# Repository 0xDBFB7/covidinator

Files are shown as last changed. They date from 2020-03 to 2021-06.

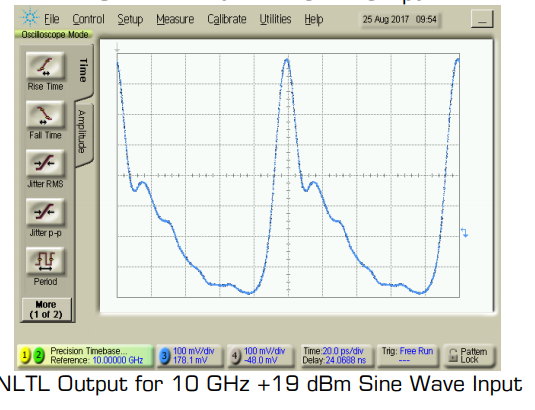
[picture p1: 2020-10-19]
electronics/propagation/NLTL_input_tone/Screenshot from 2020-10-18 20-32-23.png

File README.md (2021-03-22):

# Update March 2021

Now shifted focus to purely electroporative effects. Please see

# [Pure electroporation](https://github.com/0xDBFB7/covidinator/releases/download/vx.x/pure_electroporation.pdf) 

Thanks!

---

Hi! Welcome! There's not a whole lot of real substance here, but maybe you'll find something useful. I hope you like it! 

This was a (in retrospect, misguided) project to determine if extremely high electric fields can produce mechanical stresses sufficient to break the viral membrane (so-called electroporation). This doesn't seem to be necessarily *completely* implausible, but it's sufficiently remote (and TRL 0) that I'm not super interested in continuing work on it given circumstances.

```
<3   <3   <3   <3   <3   <3   <3   <3   <3   <3   <3   <3   <3   <3 
```

# [Terse summary](https://github.com/0xDBFB7/covidinator/releases/download/vx.x/summary.pdf) 
# [Full paper with supplemental, unfinished](https://github.com/0xDBFB7/covidinator/releases/download/vx.x/paper.pdf)

## References & Resources [HTML](https://raw.githubusercontent.com/0xDBFB7/covidinator/master/documents/references.html) | [Zotero (categories!)](https://raw.githubusercontent.com/0xDBFB7/covidinator/master/documents/references.rdf) | [BiBTeX](https://raw.githubusercontent.com/0xDBFB7/covidinator/master/documents/references.bib) 

```
<:  ^_^  :>  ^_^  :>  ^_^  :>  ^_^  :>  ^_^  :>  ^_^  :>  ^_^  <:
```

Things that are here:

 * A cheap (~$300) synchronous photon counting fluorescence reader - just a crappy plate reader/Gel-Doc/spectroflurometer without the spectro- part. 
    - Can instantly quantify sub-nanogram quantities of dsDNA using Biotium GelGreen (Xu et al's fast phage titer sampling, score!).
 * Li et al's 600-picosecond avalanche transistor Marx pulser
 * A few microbiology protocols - E. coli and T4 bacteriophage.
 * A cheap (~$300) 6-12 GHz microwave absorption spectrometer / scalar network analyzer. Almost useless for small signals, does not provide the SNR required for biological purposes, don't build one.
    - firmware/eppenwolf/runs: Data from a number of data-taking runs of the Eppenwolf.
 * A wrapper around flaport/fdtd's awesome electromagnetics library:
    - tissue.py: supports import of IT.IS Foundation computational phantom voxel files, with their supplied Cole-Cole dielectric model, for tissue simulations. Pretty rough, not formally validated.
    - PCB.py: A test of coupled NGSPICE - adaptive timestep and direct KiCAD netlist import and probe/source creation. Currently totally broken.
 * biology/JAMES/ A bespoke MD program thanks to the not-invented-here syndrome. Not enough time was spent exploring GROMACS and LAMMPS features for bead-spring elastic models. A complete waste of time. There is zero reason for this to exist.
 * Reasonably bad note-taking. When all this is over I wanna make a real sweet lab notebook, the current offerings aren't, in my opinion, super great - suggestions for features and workflows are welcome!

```
<3   <3   <3   <3   <3   <3   <3   <3   <3   <3   <3   <3   <3   <3 
```

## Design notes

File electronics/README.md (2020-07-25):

Milling settings:

30 degree carbide V-bit, 24 Krpm, 300 mm/min, 0.1 mm step-over, -0.1 mm step-down.

Check "Use aux. axis" in KiCAD gerber export, 

Todo: make a flatcam shell-file http://flatcam.org/manual/flatcamshell.html

G-code generated with FlatCAM, probed with Autoleveller 0.8.7 (bug in later versions),

then postprocessed with invert_probing.sh.

Board clamped to skim-cut MDF sheet and cut with regular scissors.

Paste stencils were laser cut from 80-weight black cardstock at 450 mm/min, 100%.

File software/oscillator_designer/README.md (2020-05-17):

To design an oscillator:

Install QUCS. QUCS 0.0.20 built from source was used.

```
git clone https://github.com/zonca/python-qucs
cd python-qucs
sudo pip3 setup.py install
```

Make a new ramdisk to avoid burning cycles on your SSD (or running into latency issues on HDD).

```
sudo mount -t tmpfs -o size=100m tmpfs /mnt/qucs-tmpfs/
```

and set net_file, net_file_modified, and data_file to that tmpfs. Also set QUCSDIR to your qucs installation path.

Design a circuit in qucs, and set schematic_file to the schematic.

This could be accomplished equally well with scikit-rf.

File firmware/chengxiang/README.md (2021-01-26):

Named Chengxiang after the team which characterized the Marx generator. (I know they weren't the first to use FMMTs as avalanche devices - I just happen to have lifted the design from them verbatim, so it seemed appropriate.)

sshfs deep:/home/arthurdent/covidinator/firmware/chengxiang/ mnt/

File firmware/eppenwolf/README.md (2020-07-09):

### The Eppendoofus

This is the firmware and host control software for the eppendoofus microwave-bio breadboard.

The d
s

the following types of messages are sent:

- Set VCO power
- ACK
-

a

Uses protobufs. Though I'm sure it exists, I couldn't find a simple
S.N.A.P protocol

Protobuf needs to be installed.
ARM_NONE_EABI doesn't like protobuf by default - no pthread! we therefore have to pass HAVE_PTHREAD=0

then we get an
google/protobuf/stubs/common.cc:50:2: error: #error "No suitable threading library available."
 #error "No suitable threading library available."
  ^~~~~
  https://groups.google.com/forum/#!topic/protobuf/WRA7uSZzC3c

Fortunately, pthread is only required in stubs/once.h; we just overwrite that, removing the relevant issues.

No go. needs lstdc++. Ultimately, just going to roll my own format.

We have to use Arduino's WString rather than std::string because of size limitations.

There has to be some packet-framing lib out there.
https://github.com/PowerBroker2/SerialTransfer - only 256 chars,

Have to remove #include "arduino.h" from SerialTransfer to mock

Now we have a real problem. We can't fit std::string on the teensy; but we can't include WString in the mocked build. So we'd either have to re-implement WString, or only use char*s, or give up on mocking.

I will do this last option.

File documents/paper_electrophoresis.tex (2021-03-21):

%!TeX root = paper_electrophoresis
\documentclass[paper.tex]{subfiles}
\begin{document}

\subsection{Paper electrophoresis}

There's a very interesting which has almost completely fallen into antiquity, and yet not obviously for any reason. Filter paper electrophoresis. It requires less work to set up than gel electrophoresis. because I believe it partially relies on a different mechanism. When power is applied to the filter paper baths, the buffer visibly pumps through. \cite{ELECTROPHORESIS1951} Electroosmotic flow 40 to 100 volts works fine, no gel needs to be poured beforehand.

I've heard that this is not effective for DNA et al, only for proteins or amino acids.

\cite{gelelectrophoresis}
\begin{fquote}
	While paper and other solid support materials proved to be an advantage over free solutions for the electrophoretic analysis of biomolecules, gels were adopted later because gels not only minimized diffusion better than paper supports they actually participated in the separation process by interacting with the migrating particles. Gels can be thought of as semi-solid matrices whose pore sizes aid in separation. The semisolid nature of the gel participates through a process known as molecular sieving. The three common media for gel electrophoresis are starch, polyacrylamide, and agarose. Of these, the starch gel medium is the least versatile whereas a wide range of separation effects can be achieved using the other two media. There are limitations to the use of both polyacrylamide and agarose but these are effectively minimized when the material to be analyzed is a nucleic acid. Even very small nucleic acids (i.e., oligonucleotides) are easily separated in an electrical field by one or the other medium. The primary criteria for choosing polyacrylamide or agarose gel electrophoresis are length and whether or not the nucleic acid is single stranded or double stranded. Short, single-stranded DNAs like oligonucleotides require polyacrylamide whereas long (>100bp), double stranded DNAs are best resolved on agarose.
\end{fquote}

The macgyver running buffer\cite{MACGYVER2005}.

\cite{Inexpensive1955}

\end{document}

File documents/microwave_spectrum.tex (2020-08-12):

\documentclass[paper.tex]{subfiles}% ===> this file was generated automatically by noweave --- better not edit it
\begin{document}

\clearpage
{\Large Experiment 1:}\\

\nwfilename{microwave_spectrum.pnw}\nwbegincode{1}\moddef{microwave_spectrum.py}\endmoddef\nwstartdeflinemarkup\nwenddeflinemarkup
import sys
sys.path.append('/home/arthurdent/covidinator/firmware/eppendoofus/host/')

import device_comms
import sweep

\nwendcode{}\nwbegindocs{2}\nwdocspar

It cannot be overstated how sensitive this measurement is. At 12 GHz, merely bringing one's hand near the coaxial line almost doubled
the power sensor reading.

\nwenddocs{}\nwbegincode{3}\moddef{microwave_spectrum.py}\plusendmoddef\nwstartdeflinemarkup\nwenddeflinemarkup
import random

\nwendcode{}\nwbegindocs{4}\nwdocspar

Positions of the three quantities on the slide are randomized\cite{first2000}.

\section{Preparation}

Autoclave

\nwenddocs{}\nwbegincode{5}\moddef{microwave_spectrum.py}\plusendmoddef\nwstartdeflinemarkup\nwenddeflinemarkup

\nwendcode{}\nwbegindocs{6}\nwdocspar

\end{document}
\nwenddocs{}

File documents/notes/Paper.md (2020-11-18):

## Field Limits

Exemption limits increase from 70 mW at 35 mm from the body to:

- at or above 6 GHz and the source-based, time-averaged maximum e.i.r.p. of the device is equal to or less than 5 W (adjusted for tune-up tolerance).

In these cases, the information contained in the RF exposure technical brief may be limited to information that demonstrates how the e.i.r.p. was derived.

At between 6 to 15 GHz, in an uncontrolled (public) environment, the Canadian government sets field thresholds at 61.4 V/m RMS. They also specifiy a limit adopted by most countries; 1 milliwatt / cm^2 (10 W/m^2) over a 6 minute averaging time, along with the following constraint:

> The total incident energy density during any one-tenth second period within the averaging time shall not exceed one-fifth of the total energy density permitted during the entire averaging time for a continuous field.

Controlled (occupational) limits are 50 W/m^2.

Uncontrolled electric field limits in Canada are 61.4 V/m and controlled is 137 V/m RMS. Yang et al's models for H3N2 specify a threshold at 86.9 V/m, but observe 40% inactivation at 87 V/m, and only 70% at 171 V/m (320 W/m^2) . All of those power densities are above even the controlled-environment power-density guidelines, at 20 W/m^2.

[https://www.icnirp.org/cms/upload/publications/ICNIRPrfgdl2020.pdf](https://www.icnirp.org/cms/upload/publications/ICNIRPrfgdl2020.pdf)

#### Exposure time

Both Yang and [] (apparently arbitrarily) chose a 15-minute exposure in their tests. To determine the effectiveness against airborne particles, and to minimize the power required in a dwelling phased-array beam, we must first establish the required duration of exposure.

As opposed to chemical inactivation, where the time dependence is dominated by viscous fluid dynamic effects [Hirose 2017], or ionizing radiation, where a certain dose of photons must be absorbed, 

As a damped, driven oscillator, the ring-up time of the virus depends on the Q factor. Yang et al. state the Q of H3N2 to between 2 and 10, so at 8 GHz the steady-state amplitude should be reached in well under 1 us.

Reality is rarely so tidy. [] have found a significant mechanical fatigue effect in phage capsids, where a small strain applied repetitively eventually causes a fracture. At low field strengths, this mechanism could extend the exposure required to break the capsid or membrane.

Variance in the sizes and stiffness of viruses (due to mutations) could shift the resonance off-peak, requiring a longer duration exposure or a frequency chirp to accommodate.

Other research[] has found T4 approximately a thousand times "easier" to inactivate chemically; however, its capsid is mechanically approx. 2x stronger than H3N2's envelope.

> [] obtain an excellent prediction using an elastic continuum method with a spherical virus, with opposite charges in core and shell.

We wished to gain more insight into the processes which cause the fracture, in an attempt to reduce the field requirements further.

Both coarse-grained bead-spring molecular dynamics (via integration of particle motion) and finite-element methods (via solution of governing elastic PDEs) have been used to great effect for simulation of mechanical properties of viruses. More recently, all-atom methods have also become computationally viable. An MD scheme was chosen for no particularly good reason.

The algebraic normal-mode methods included in many software packages [charmm] are not generally sufficient for this task, as they often assume the limit of low-amplitudes.

LAMMPS, GROMACS, OpenMM and HOOMD-blue were evaluated, and all could been made to work with some modification. However, because of difficulties in defining new force-fields for coarse-grained bead-spring modelling, because of the specific time-domain electric field impulses desired, and because of the multiple-run frequency sweep required to optimize the impulse, a custom simplistic MD code was written.

Unfortunately, electric polarization effects, (the redistribution of electrons)

The phage model was produced from raw CryoEM data using ProDy. ~~The coronavirid model was produced with LipidWrapper.~~

[] Each field seems to invent its own terminology for multiscale modelling. "coarse-graining" is referred to as DSMC.

[]: the use of special symbols in names seems to be problematic for searches. Hereafter we will refer to \phi 6 as Phi6.

----

It remains to be seen how much not-invented-here fallacy was baked into this project.

### [How long do T4 phages in the provided packaging last when refrigerated? Thanks!](https://www.carolina.com/viruses/coliphage-t4-t4r-living-5-ml/124330.pr#)

1answer

1. CBS Ben

   · 11 months ago  

   They can be refrigerated up to a year without any change in labeled titer.

double-wide, with 'resources' and 'figures' on the right pane? Emphasizes other documents
and figures more

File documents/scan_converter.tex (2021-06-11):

%!TeX root = scan_converter
\documentclass[paper.tex]{subfiles}
\begin{document}

\section{Scan converter}

\begin{autem}
This is an example of how the course of action can be distorted by engineering. In a non-pandemic scenario such a diversion might have been a reasonable. Indefensible. I am consoled that it did not account for more than 2 to 3 weeks of work.
\end{autem}

\begin{autem}
	This section is deliberately kept vague and without reference to construction details to avoid export restrictions. In any case, it is hard to imagine a technique fully developed and published in the 1940s would be of great secrecy now. 
\end{autem}

Because of the small sizes of viruses, all interesting time-domain spectroscopy results require resolving signals with greater than 10 GHz bandwidth.

So called "equivalent-time" or "sampling" oscilloscopes are less expensive; but it was hoped that it would be possible to resolve the breaking of the capsid - a transient, single-shot phenomenon -   A digital oscilloscope capable of real-time sampling such a transient is a tall order, and it did not appear that an undergraduate would be allowed access.

Gating time. Photoconductive gating is a particularly interesting technique for this.

There is also the concern that, when measuring a system producing kilovolt pulses using an instrument with an extremely electrically delicate 1V maximum input, some harm might come to a machine worth more than the experimenter. 

This turned out to be not unfounded - the kilovolt pulser used was observed to cause the RPi controlling the experiment to 

However, transient recordings of sub-nanosecond phenomena were made as early as 1938 by Manfred Von Ardenne using a "micro-oscillograph". By 1946, such oscillographs - now with bandwidths in excess of 10 GHz - were readily available commercially\cite{3beam1946}, and by 1949 found extensive use for quantitative measurements of ultrafast phenomena by Fletcher\cite{Production1949} and others. 

"Direct access" tubes to the logical conclusion. The design of Fletcher puts the cathode ray deflection plates essentially inside the.

The main practical limitations on oscilloscope sweep speed are discussed by Mackay\cite{New1948}, and are imposed by the Y axis deflection plate electron transit time and bandwidth (the X-axis speed is of less importance), and the beam current and sensitivity of the phosphor (faster sweeps reduce the electron flux and brightness of the dot).

\begin{figure}[H]
	%	\makebox[\textwidth][c]{
	\centering
	\subfloat[Damage to the sensor, believed to be due to. ]{
	
	
}
	\hfill
	\subfloat[]{
		
		
	}
		\hfill

	\subfloat[Direct electron beam detection]{
	
}
	\caption{Second.}
		\hfill

\end{figure}

\begin{figure}[H]
	\captionsetup{singlelinecheck = false, justification=justified}
	\centering
	
	\caption{}
\end{figure}

\begin{figure}[H]
	\captionsetup{singlelinecheck = false, justification=justified}
	\centering
	
	\caption{}
\end{figure}

The very high voltage actually makes this much easier

means that low-sensitivity diagnostics, like lithium niobate optical probes. Not having a suitable optical bench, an electron-beam probe, similar to a streak camera, itself similar in principle to scan-conversion digitizer tubes in Tek SCD and 7912 series transient digitizers.

If a low voltage sensitivity is required, and because modern high-pixel-density CMOS sensors allow the required deflection (and therefore the entire structure) to be minimized, these are simple to design and inexpensive (much of the complexity is in the slow-wave or travelling-wave structure which is usually required to match the signal velocity to the - slowing down light without affecting its properties or drawing power is an extremely difficult problem) and can offer sample rates in the terasamples/s and analog bandwidths of many dozens of GHz, albeit with very low vertical resolution. 

original von Ardenne 

\begin{fquote}[Livermore Operations][\cite{Scan2008}]
An internal CCD recorder would provide high sensitivity to the swept electron beam, but a CCD in a sealed vacuum tube has never been attempted or demonstrated in the phototube facility at Livermore Operations (LO). A prototype tube would most likely be built with a phosphor screen.
\end{fquote}

Possible routes:

make the plates super small like Von Ardenne (thin wires). see the papers on thin wires.

make the plates slow-wave structures matched to the speed of the electron; travelling-wave deflection plates.
unfortunately, travelling wave structures necessarily absorb power and affect the impedance of the circuit in question

multiple beams with different path lengths to have different phases?

put the x-axis at a 45 degree angle?

radiation damage to sensor 

Possibly some optical method. 

however, recording such transients is quite a solved problem, having been accomplished to the required degree 

taking "direct access" tube to its logical conclusion.

since the sensor will inevitably outgas, a sealed tube is impractical.

Low vacuum, gas focused tubes are less predictable and more difficult to model. XOOPIC; the standard PIC code WARP has undocumented feature of collisional ionization but Tegerup has a guide to use. Simulation

PIC-LAS

The distortion due to transit-time phasing is

$$ \frac{\sin(\frac{2\pi F \tau}{2})}{(2\pi F \tau)/2} $$

where $\tau$ is the transit time of the electron through the deflection region 

Image intensifier microchannel plates where angled holes cause secondary electron 

stray light 

old canal ray paper

the old WARP has a module for collisional ionization, though it's got a bug \cite{Simulation}.

\end{document}

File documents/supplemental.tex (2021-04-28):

%!TeX root = supplemental
\documentclass[paper.tex]{subfiles}
\begin{document}

\clearpage
%%%%%%%%%%%%%%%%%%%%%%%%%%%%%%%%%%%%%%%%%%%%%%%%
%%%%%%%%%%%%%%%%%%%%%%%%%%%%%%%%%%%%%%%%%%%%%%%%
\section[Appendix]{\Huge Captain's Log, Supplemental}

%%%%%%%%%%%%%%%%%%%%%%%%%%%%%%%%%%%%%%%%%%%%%%%%
\begin{fquote}[Paraphrased from W. G. Cochran][\cite{Statistical1953}]
The accumulated insight of a worker frequently merits recording when no documentation can be given.
\end{fquote}

%tonsil

\section{Sensing}

There is little discussion on microwave virus detection, with the notable exception of [Mehrotra 2019]. 

However, \cite{Microwave2012} find that - in controlled conditions - they can detect a single E. Coli bacterium in 50 uL of broth via a microwave cavity. 

Havelka \cite{Highfrequency2011} discuss microtubules.

With an extremely high power excitation pulse, the problem may become somewhat easier; especially if the virus has a ring-down that can be subjected to autocorrelation.

However, the dipole radiation power expected in even the most implausibly optimistic case would be about as follows:

$$P={\frac {\mu _{0}(2 \pi \cdot 20 GHz) ^{4}(0.5 \text{nm} * 10^6 e^-)^{2}}{12\pi c}} = 7.1 \times10^{-16} \text{W} $$

which for most reasonable conditions would $\approx 0.5 Janskies$, meaning that the power radiated from the virus would be considerably overpowered by the milky way.

% (magneticConstant*(2 pi * 20 GHz)^4 * (0.1 nm * 1000 * electronCharge)^2)/(12*pi * c) -> W

Materials

polycarbonate

infinitely autoclaveable. However, clear has possible issues with flurosescence background. white 
is 
generally recommended for fluro. 

polypropylene
autoclaveable, although softening causes warping if not supported. Difficult form strong bonds to 
with adhesives. causes "hairs" when machining.

Rationale for doing this alone. Science is nothing without collaboration. However, it's also nothing without acknowledging the shortfalls of your research. There remains no physical reason to expect this to work - it is indistinguishable from crackpottery - and, in fact, the first route of investigation did not work. Therefore, seemed irresponsible to redirect resources or involve other people.

at least that's the story I tell myself.

There is some good advice in the Government Accountability one is especially sage:

"Be as quantitative as possible."

source of truth in the home lab. For instance, you can build an oscilloscope, or a pulse generator, 
but not both. 

\subsubsection{Old papers}

many of the base facts - and some of the most useful and simplest methods - are in the early 
papers, and later papers generally just refer to the previous ones. it can be of some use to try to 
find the earliest papers. 

For instance, when searching for methods for the bacteriophage, lots of modern detail-scarce papers 
appear, but none of the most important Delbruck papers. Books are one way to side-step this issues

When searching for old papers, use the terminology of the day. millimicrosecond, for instance, for 
nanosecond".

find government gray-literature publications on the topic. They are often 

find research groups with "lists of publications".

\subsubsection{Cargo-cult}

For in-vitro research, it seems to me that perhaps this field is running into the issues Feynman's rat-races \cite{Cargo}. There are a large number of very tricky variables. Requires analysis fo the very details of how the study was conducted, rather than simply its results. While the measurements 

Of course, we commit the very same mistakes and fall into the same traps, we are not immune from criticism.

In some cases, these are thoroughly characterized and described. UWB rat paper. 

But it seems to me that each worker (myself included!) is using their own test arrangement; and yet the studies are not so different as to require such customization.

It occurs to me that perhaps a set of exquisitely characterized standardized test cells and procedures would be helpful; and a requirement that any papers on the topic either use such a cell, or if their study requires some exceptional treatment, to follow an established procedure to add a new cell to the standard. 

Alternatively, methods such as the optical hetrodyne one,

If possible, very specific buffer compositions should be made universal.

What heating patterns can be expected from a certain microwave input? What modes can be introduced by deviations in machining tolerances?

Then, of course, are the questions of the excitation: what brand of attenuators are satisfactory?

Of course, one cell could not suffice for the whole range of microwave frequencies.

There is also the matter that the scientific publishing infrastructure could perhaps provide for a "scientific lineage". We often hear of a "scientific record": journals will retract a paper from "the record"; but where {\it is} this record? Where is the chain of trust upon which new results can be added? Each paper is forced to supply its own context; each worker is forced to re-dredge the entire chain of truth, to discover the controversy which clouds some papers; each offers its own interpretation of the literature. It is inevitable that some history will be lost; that the wrong starting point will be taken up; a veritable fork in the literature. Especially as the volume of scientific research increases as society proceeds. The only data is a few references per paper, and a date for each! Another such record exists in comprehensive books written by workers on the topic.

But is this not an artifact of the limitations of printed journals, whereby papers must necessarily be individual entities? Is there no way by which papers can be arranged so that they each supply a visible part of the jigsaw, where each paper brings with it the complete story of the field?

Scite.ai and similar services, but it feels like these are tacked-on workarounds to re-add metadata which should have existed in the first place.

Consider the non-thermal effects literature. It starts, perhaps, in the 1800s; 

\clearpage
%%%%%%%%%%%%%%%%%%%%%%%%%%%%%%%%%%%%%%%%%%%%%%%%
{\Large Optical centrifuge polarization chirp}\\
\begin{multicols}{1}
%%%%%%%%%%%%%%%%%%%%%%%%%%%%%%%%%%%%%%%%%%%%%%%%

\includepdf[
    %% Include all pages of the PDF
    pages=-,
    %% make this page have the usual page style
    %% (you can change it to plain etc). By default pdfpages
    %% sets the pagecommand to \pagestyle{empty}
    pagecommand={\thispagestyle{empty}},  
    %% Add a "section" entry to the ToC with the heading
    %% "Quilling Shapes" and the label "sec:shapes"
    addtotoc={1,section,1,Quilling Shapes,sec:shapes}]
%% The pdf file itself
{optical_centrifuge.pdf}

\includepdf[
%% Include all pages of the PDF
pages=-,
%% make this page have the usual page style
%% (you can change it to plain etc). By default pdfpages
%% sets the pagecommand to \pagestyle{empty}
pagecommand={\thispagestyle{empty}},  
%% Add a "section" entry to the ToC with the heading
%% "Quilling Shapes" and the label "sec:shapes"
addtotoc={1,section,1,Quilling Shapes,sec:shapes}]
%% The pdf file itself
{biology.pdf}

\end{multicols}

Contrary to some [Hardell 2017] reports, we do not find the FCC and ICNIRP to be significantly affected by special interest groups; their rationales appear to be transparent.  [FCC-19-126A1], for instance, is a particularly entertaining memorandum:

\begin{quote} 
	
Similarly, IEEE-ICES urges the Commission to adopt a higher SAR exposure limit of 2 W/kg averaged over 10 g. [snip] We are not persuaded that the IEC standard should be adopted at this time.", "Medtronic and the AAMI-CRMD recommend a more relaxed threshold of 20 mW. We decline to increase the 1-mW threshold.". 

\end{quote}

Things heating up at the Microwave Safety fandom.

\clearpage
%\rule{\linewidth}{0.2pt}
%
%
%There seems to be a discrepancy between \cite{Efficient2015} and our reading of [C95.1-2005].
%
%They use a threshold in open public space of $100(f/3)^{1/5} \text{ W/m}^2$. The 115 W @ 6 GHz figure they provide corresponds to this equation with a coefficient of 100.
%
%For Table 9, general public, the equation is $18.56 (f)^{0.699} \text{ W/m}^2$, or $64.93 \text{ W}/\text{m}^2$ @ 6 GHz. 
%
%Different versions of the IEEE standard have used equations of equivalent form but with different coefficients [Wu 2015]; it is entirely possible that we have retrieved the wrong standard.
%
%\rule{\linewidth}{0.2pt}

\section{Wherein a wideband oscillator is designed}

Several incorrect pieces of information conspired to lead us to try to develop an inexpensive ultrawideband oscillator.

\begin{itemize}
	\item The
	\item The assumption that a broadband frequency sweep would drastically improve the inactivation threshold, and moreover that 
	\item The ideal 
	\item The assumption that the only commercially available oscillators in this frequency range were expensive YIG-tuned devices.
\end{itemize}

Besides the AD (formerly Hittite) HMC732 device, ADF5355 and lmx2615

There are really two different conflicting criteria: 

A low-cost, wide-band

Unfortunately, designing wideband microwave circuits is significantly more difficult than for a particular frequency. Quarter-wavelength 

Varactor diodes are a GaAs hyper-abrupt junction diode.

We were warned that this would be difficult: 

CEL did not supply a SPICE model for the GaAs FET device used in early prototypes. A FET was originally because a gate is ostensibly easier to bias than a base; but this turned out to be unfounded.

[Steenput 1999] has an interesting analytic method to synthesize a SPICE model suitable for a transient simulations from S-parameter measurements using negative resistances. However, this neglects the I/V characteristic. 

[Polyfet 1998] describes a simple optimization method to synthesize a SPICE model for an active device, and CEL appnote provides some details for GaAs devices.

\rule{\linewidth}{0.2pt}

OpenEMS is excellent, with Python bindings, some lumped components, and mesh refinement. However, embarrassingly, we were not able to resolve all the dependency issues in order to install it.

\paragraph{Biasing}\

In our simulations, the varactor-tuned feedback circuit appeared to be particularly sensitive to the introduction of bias-tees. 

The gate must be weakly pulled to ground, otherwise stray charge destroys the oscillation.

\fancyhead[C]{style 1 with thin line}

With 0.79 mm FR4 substrate and 0.2 mm (8 mil) wide traces, the maximum impedance achievable was about 115 ohms, which did not appear to be sufficient as an RF choke. Use of defected grounds can increase inductance, but this was not evaluated.

If suitably high-impedance traces are not available, a common technique is to use a quarter-wavelength line (approximately 6 mm long with the above parameters at 8 GHz) terminated with a stub to produce a virtual short or open circuit [Seo 2007]. 

However, reflections from these structures still appeared to distort the frequency/phase response beyond repair, even with ostensibly wideband stubs [Syrett 1980].

\noindent\fbox{\parbox{\linewidth}{
	Rebuke: despite this blather, many other papers have had success with bias-tees at these frequencies.
}}

Alternate methods evaluated, failures: 

In production, these could be accomodated by graphite-polymer printed resistors. 

Odd-pole varactor-loaded combline filters appeared to have excellent phase and frequency response; however, the geometry necessitates low-inductance via stitching to the ground plane.

%\noindent\fbox{\parbox{\linewidth}{
\begin{autem}
	{\it autem} Others have had great success with varactor-tuned comblines, especially non-grounded lines.
\end{autem}

[Tsuru 2008 fig. 10] is an excellent review of various oscillator designs.

The parasitic inductance of common varactors appears to become problematic at these frequencies (but not for non-wideband use).

\paragraph{\textbf{Spacing}}\

FDTD results still yielded some coupling at 2 mm isolation.

\paragraph{\textbf{Via stitching}}\

Rather than the almost universal technique of via stitching components immediately to the ground plane (a tedious process with our prototyping setup), a large ground pour on the component layer was used wherever ground was needed, as mentioned in [Hunter? combline]. Since we use microstrip rather than coplanar waveguide, 

Since the ground plane does not participate in the DC bias at all, no vias are required in the final device. This means that the drilling, electroless strike and electroplating steps are unnecessary for production.

\PRLsep{{\itshape The wideband oscillator }}

Not having access to any RF equipment, we needed an oscillator tunable over the X-band.

There are many oscillators. The HB100 uses a dielectric resonator, for instance; cavity-based methods with mechanical tuning; active antennas using. 

The literature is quite mature, partly due to the FCC's recent ultrawideband communications guides.

As a result of our gross incompetence, the oscillator was designed via an inane, roundabout, and fiendishly tedious manner, and our description of this technique only contributes to the field by being suitable for a dartboard; our analysis can only hold water when combined with paper mache; and a lesser invertebrate in posession of a copy of Grebennikov's excellent Microwave Oscillator Design would have accomplished the task faster.

Designing an oscillator of this type in one step with a few kindergarten equations appears to be well within the reach of modern network analytical techniques. Genetic algorithms are quite well matched to this problem, and many commercial software packages are  [computer microwave design book]. 

We began experimentally by building a scaled version of [Mueller 2008]'s active antenna crudely with copper tape, using a CEL [] GaAs FET.

We then manually tried a number of filter designs, using the manufacturer's S-parameters and QUCS' microstrip approximations. This intially appeared to yield good agreement with experiment. Peaks in the feedback voltage simulation corresponded approximately with peaks in the observed spectrum. [figures from LO prototype N]. 

A crude, inane, and extremely disorganized trial-and-error procedure was performed for many weeks. A wide variety of analytical methods for filter design were attempted [documents/global.ipynb], but simultaneously obtaining the correct phase shift and frequency response was somewhat difficult. Adding the parasitic inductance of the varactors always seemed to destroy our most perfect creations.

Using an SIR filter has the added advantage of confusing epidemiologists.

Eventually, QUCS, zonca/python-qucs, and scipy's basinhopper were used with a cost function somewhat similar to that described in [Kaplevich]:

\begin{verbatim}
    freq_coeff = 1
    phase_coeff = 1.5
    ratio_coeff = 0.5
    insertion_loss_coeff = 0.2
 
    frequency_cost = freq_coeff * (abs(desired_center_frequency-fb_peak_frequencies[0])/1e9)
    phase_cost = phase_coeff * abs(1.0 - phase_at_peak)
    ratio_cost = ratio_coeff * fb_peak_ratio
    insertion_loss_cost = insertion_loss_coeff*(1.0 - fb_peak_values[0])
    cost = frequency_cost + phase_cost + fb_peak_ratio + insertion_loss_cost
\end{verbatim}

Optimizing first for the high frequency, fixing the inductor and microstrip values, and then optimizing for the varactor values at the low frequency.

This produced a seemingly acceptable feedback loop (note the group delay / phase progression):



However, when this was built, varactor tuning performance was abysmal, with hops and peaks; and the tuning range was far smaller than expected.

It was thought that a transient simulation - to determine how the spectrum actually evolved - would improve the situation. 

As of 0.0.20, QUCS' microstrip models are not yet compatible with transient simulations; and some improved filter designs required simulating coupling between more than two microstrips, which QUCS did not yet support natively.

\begin{figure}[H]

\end{figure}

The complete transient simulation matched reality very closely. 

\begin{figure}[H]
	\includesvg[width=\textwidth]{wideband_LO_2_simulated_tuning}
 	\caption{"Wideband VCO 2": BFP620  \\
 	 Oscillator tuning simulated with electronics/ngspice/oscillator\_designer\_2.py commit <>, eLabID 20200613-d28a8004c...}
\end{figure}

The oscillator design is a testament  This highlights that a computation is not a substitute for understanding.

The key sticking point seems to be that as frequency increases, using microstrip design techniques, the parasitics of any filter structure are so large that the small change in impedance that the varactors can provide does not tune the circuit by any meaningful amount.

The two varactors on each tuning circuit each contribute 0.7 nH and between 0.35 to 2.4 pF; each blocking capacitor contributes about 0.2 nH. The frequency range of the oscillator can be selected by adding between 0.5 nH to 1.5 nH symmetrically to both tuning circuits. 

"Using the lead inductances of the bipolar transistor and varactors provides the required value of the base inductance".

Indeed, [Tsuru 2008]'s "tuned circuit" in Fig 8 is, in fact, just the varactors, plus an almost invisible high-impedance line.

The final oscillator is a 'wideband double-tuned varactor VCO', based almost verbatim on [Tsuru 2008] and the reference design in Figure 8.36, p378 of [Grebennikov 2007]. 

The rest of the papers in the bibliography were highly enlightening regarding the principles of microwave oscillator design.

For ease of design and simulation, selecting a device with both Touchstone S-parameters and SPICE models is greatly preferable.

It is commonly claimed that FR4 is a 'slow' substrate, and that the high loss tangent of ~0.02 makes it unsuitable for microwave systems.

However, with this PCB substrate, the expected loss of only 0.026 dB/mm on signals of minimum 0 dBm is patently acceptable. As viruses do not have a discriminating palate, we are also only minimally concerned with $S_{11}$ reflections, noise, or spurs, so precise impedance control is not required; the wideband VCO sweep accomodates for any variations in resonant frequency due to wide manufacturing tolerances.

This topology of oscillator worked marvellously on essentially the first try.

Not having a good analytical understanding, we resorted to using a purely computational method.

In addition, the design of wideband feedback-loop VCOs is a relatively well-explored field, and many reference designs exist. 

Merely scaling designs like [] was not effective.

Several analytical filter design methods were 

This is apparently known as a "double-tuned" wideband.

Oscillators must meet the Barkhausen criterion:

\begin{itemize}

\item A 360 degree phase shift around the feedback loop (including the phase shift contribution from the amplifier, which itself varies greatly with frequency)
\item A loop gain $>1.$ 

\end{itemize}\
%
However, in practice a third element is also required:
%
\begin{itemize}
\item A frequency-selective element that restricts oscillation modes and decreases phase noise.
\end{itemize}
%

With large feedback-loop structures, such as long PiN-switched phasing lines, proximity effects from nearby flesh were found to detune the oscillator significantly.

 design of a triple-tuned oscillator.

\paragraph{}
The buffer amplifiers 

\rule{\linewidth}{0.2pt}

In case you're wondering, like I was, why the voltage coefficient of capacitors 

\rule{\linewidth}{0.2pt}

Much of this project was done in 1.5 mm microstrip with a 2.5 to 3 mm routed isolation. However, it became apparent that the inductance of vias with the ground plane was too great. It has been suggested that low-inductance vias in prototypes \cite{Microwavee}

Grounded coplanar waveguide, where the primary ground plane is on the top side of the board, presents many advantages, and in later testing appeared to provide much better performance and easier design. connectors can interface with the top side; trace sizes are much more compatible with small SMD devices.

\rule{\linewidth}{0.2pt}

Again, inductive choke biasing in the feedback loop was practically impossible. Biasing PiN diodes with a 10kohm resistor, (with 330 ohm safety resistor) one to 48V bias and another through an 2N7002P N-channel mosfet worked fine. 

The oscillator ran fine with a PiN bias of 2.34 mA. [LO prototype N]. A high bias voltage of 48V was required to get sufficient current through the two 10K resistors and the PiN diode to obtain a low impedance while remaining delicate with the vfb.

The PiN diode used has a resting resistance of 500 ohms, 5 ohms at 2 mA and 2 ohms at ??. 

48V is a little tight on the 50V rated voltage of our DC blocking capacitors.

Each activated PiN diode should be biased separately, since putting 2x 2 mA through 20K would take an impractical 80V.

\rule{\linewidth}{0.2pt}
%
%Conductors are represented by zeroing all components of the electric field in those regions. 
%
%There are many different possible source geometries, each introducing their own distortions.
%
%There are many ways of linking SPICE and FDTD. 

\rule{\linewidth}{0.2pt}

Bandpass filters can be designed by first designing a low-pass filter prototype (usually Chebychev) (or, in our case, using reference filter component tables), and then transforming this low-pass into a band-pass. [Hunter 2001] is an excellent overview of this process, with many design examples for different filter topologies. 

The coupling coefficient between two low-pass filters determines the band-pass bandwidth.[Hui 2012]

[Hunter 2001] also describes an analytical method to create a filter with the precise group delay - phase shift versus frequency - required for stable oscillation. However, simultaneously compensating for the group delay introduced by the amplifier itself (nearly 180 degrees over the frequency range for the CEL part) seemed complex.

Phase shift can be introduced either via a length of microstrip, or a high-pass/low-pass filter [Microwave101]. Adding a fixed microstrip line restricts the tuning range, however, and the filter inevitably affects the frequency response.  

%\rule{\linewidth}{0.2pt}
%
%NGSPICE's KSPICE coupled transmission lines require the capacitance and inductance per unit length in Maxwell matrix form, rather than the physical $C_{even}$/$L_{even}$ (each line's capacitance and inductance to ground) and $_{odd}$ (between elements) form provided by tools like wcalc. "matrix not positive definite". [Schutt-Aine] discusses this; we reproduce here for convienience.
%
%\[ L_{11} = L_{22} = L_{even}  \]
%\[ L_{12} = L_{21} = L_{odd}  \]
%\[ C_{11} = C_{22} = C_{even}+C_{odd}  \]
%\[ C_{12} = C_{21} {\it{(unused)}} = -C_{odd}  \]
%
%\rule{\linewidth}{0.2pt}
%
%In practice, the timestep required to obtain convergence in particularly tight corners of the SPICE simulation can drop to 1e-20, which is far below the Courant limit of the FDTD simulation. To eek out a bit more performance, a simple adaptive-timestep technique from [ a ] is used; we simply set the timestep so that the maximum change in voltage per timestep from the SPICE portion is less than 
%some threshold.

\PRLsep{{\itshape Sampling time-domain spectrometry}}

\begin{quote}
A rapidly increasing voltage step V tŽ . is applied to the 0
line and recorded, along with the reflected voltage R tŽ .
returned from the sample and delayed by the cable propagation time Figure 2 . Any cable or instrument artifacts Ž .
are separated from the sample response due to the propagation delay, thus making them easy to identify and control. The entire frequency spectrum is captured at once,
thus eliminating drift and distortion between frequencies.
\end{quote}

The pulse is usually recorded in real-time with a many-GHz oscilloscope. However, by using a sampling oscilloscope, massively undersampling the signal,

Another advantage of this technique is that no high-Q filters are required to select the frequency;
discrimination is in the time-domain, and is spread out over many seconds. It is also much easier to generate a 10+ GHz fast edge than it is to generate a CW signal.

\PRLsep{{\itshape Power amplifier }}

The amplifier and oscillator are separate for ease of design; this way the phase response of the amplifier is of no consequence. 

Our target power for the test is about 0.01 W, mandating a $2 \sqrt(2)$ V peak to peak RF swing on the Z=50 output.

The $V_{CEO}$ breakdown of the bipolar transistor in question is only 2.3V. Above this value, current begins to flow from the emitter to the base, turning on the transistor and causing thermal runaway. If the base bias has a low enough impedance and can source current, this $V_{CEO}$ can be violated safely. [Toshiba, Bipolar Transistors, some other paper on the strong base bias]

One solution would be to match the output to a lower impedance [Leuschner 2010]:

\begin{quote}
Generating high RF power from low supply voltages poses also another problem: the optimum load impedance of the PA output stage transistors becomes very small. A matching network with a high transformation ratio is needed to transform the antenna impedance of 50 to the optimum load impedance. High transformation ratios usually result in small bandwidth and higher losses. Possible solutions are the use of either non-standard high power RF devices or special circuit topologies using only the available standard devices.
\end{quote}

Use of so-called stacked, HiVP, or collector-feedback cascode designs can also allow the RF voltage to be distributed over many devices.

It should also be noted that when stressed, these devices can fail with a slow power-output degradation over weeks, an effect not usually found in lower-frequency designs. 

%\printbibliography[heading=none, title={}, keyword={amplifier}]

%
%\clearpage
%\PRLsep{ Wherein antennas are characterized}
%
%Method-of-moments solvers like NEC-2 are the standard for simulating these sorts of antennas. However, most commonly-available packages don't seem to handle multiple dielectric constants, such as the air and substrate of a patch antenna.
%
%The impedance of a structure over frequency can be determined in FDTD by:
%
%\begin{itemize}
%  \item Applying a gaussian pulse to a voltage source - in our case, applied to a via connecting the path (or probe)
%  \item Running the simulation until the transients have all died out below some threshold, while logging the source voltage and current at each timestep
%  \item Taking the fourier transform of the (real) excitation voltage and current (producing a complex result, mind you)
%  \item Taking the magnitude of the ratio of the two complex spectra.
%\end{itemize}
%
%This is the computational equivalent of dropping a piano off a balcony to see which key is stuck.
%
%See [Penney 1994], [Luebbers 1992], [Luebbers 1991], [Luk 1997]. 
%
%Our implementation is in \ghfile{electronics/simple_fdtd/runs/U.py}.
%
%A similar mismatch to the SPICE exists for fourier methods - but in the other direction.  The courant limit often demands fine timesteps, but since each FFT bin is $ f_{bin} = n_{bin} / (N_{simulation} \ dt) $ , the majority of the FFT bins exist into the hundreds or thousands of GHz, leaving no resolution in the low-frequency domain of interest unless $N_{simulation}$ is extremely large - even if all the transients in the simulation have died down, you still have to keep the sim running to make the FFT happy! 
%
%There's more than enough 'information entropy' in 4000 FDTD points for most antennas. But you need some 30,000 points to get 10 bins below 20 GHz!
%
%There are a few methods of changing the FFT bin size artificially, which [Bi 1992] reviews. You can "use a manual fourier integration over the frequency region of interest".
%
%But, in a staggering turn of events which will presumably be familiar to statisticans and preposterous to everyone else, a far simpler method is to {\it discard} 95\% of the data, by down-sampling to 1/10th or so.
%
%An equally simple method that seemed to produce better results in our case is to pad the voltage and current samples to the correct length. The jump discontinuity introduced by padding with zeros has a negligible effect.
%
%It's so thumpingly unintuitive to me that adding 50,000 zeros to a 5000 value dataset can improve the resolution of a measurement by 300-fold.
%
%It is important to remember to normalize the gaussian pulse, or else numerical noise will be introduced. The magnitude is not important - [Luebbers 1992] use 100v, others use 1v, etc.
%
%Though uneven dt FFTs exist, the time step can be constant at the courant limit for this simulation.
%
%A step impulse (1 first timestep, 0 otherwise) has been used in some works, though in our case performance was quite horrid.
%
%A correction factor due to the staggered magnetic field of the Yee lattice must be introduced; [Fang 1994]. Their $Z_2$ equation (correcting for spatial inaccuracies, but not temporal) was sufficient.
%
%
%This technique is equivalent to that used in electrochemistry, known as fourier impedance spectroscopy - except they seem to usually use a known impedance source rather than a hard source, presumably because ideal hard sources don't exist in reality.
%
%Allowing the simulation to run for long enough that all transients dissipate is important for accuracy - deceptive dips in the current can cause early termination. A surprising amount of detail is contributed by even the smallest current levels. Our threshold is 1e-7 amps for 700 iterations.
%
%[Samaras 2004] has a very useful set of experimental and FDTD data for calibration and comparison. Comparing a probe via source in the different positions, we obtained agreement of $\sim 7\%$ in impedance and $\sim 5\%$ in frequency.
%
%The use of a hard source feed-port affects the number of timesteps required by introducing unphysical transients. Using a port with a virtual 50-ohm resistance reduces the computational requirements by a large factor; see [Luebbers 1996].
%
%Simply monitoring the source current during the simulation is somewhat deceptive. Periodically monitoring the change in the fourier transform seems to be a better convergence metric.
%
%The units of the FFT (unlike those of the continuous FT) remain in volts.
%
%\rule{\linewidth}{0.2pt}
%
%Most equations in papers on the FDTD method are supplied without making the scaling factors explicit; some need multiplying by the Courant number, For use with flaport/fdtd the H-field to current line integral in [] requires scaling by $\mu_0 * (dx/dt)$, where $\mu_0$ is the vacuum magnetic permittivity, dx the cell size, and dt the timestep - despite the equation already possessing a deceptive set of $dx$-es.
%
%FIX THIS IT'S WRONG
%
%Naturally, if one is competent, this discrepancy will be immediately obvious. Those not dimensionally-intuitive, such as myself, find it useful to run dimensional analysis using a unit-aware calculator such as {\it sharkdp/insect}.
%
%\rule{\linewidth}{0.2pt}

\begin{quote}
With four parameters I can fit an elephant, and with five I can make him wiggle his trunk.
\end{quote}
- von Neumann  

with six parameters, you can do it with only physical constants. Beware numerology.

\rule{\linewidth}{0.2pt}

Most passives (inductors, capacitors) companies supply S-parameters for their parts. Use them.

\rule{\linewidth}{0.2pt}

This has nothing to do with , but it's an amusing parlor trick that I accidentally ran into while trying to carbothermally reduce copper oxide powder. It led me to the SiC susceptor resonator, so it wasn't a total waste.

Add a thimblefull of fine copper powder to the bottom of a mason jar. Cover the mouth with a layer of Kapton tape. Next, inject pure argon gas for a few minutes, then seal the tape fully.

Put the whole shebang in a friend's microwave oven. 

Wait patiently. There will be a sizable bang and a terrific plasma.

My hypothesis is that this is due to the higher ionization energy of Ar. Air seems to slowly leak in, decreasing the 

\PRLsep{{\itshape The antenna itself }}

The impedance of a patch antenna varies with position on its surface. Probe feeds to a specific point on the patch

Unfortunately, patch antennas have a relatively narrow bandwidth.

\rule{\linewidth}{0.2pt}

\PRLsep{{\itshape Power sensing }}

The diode detector power sensor is based on the Infineon appnote [] and [], itself based on a circuit from The Art Of Electronics. 

A detailed description of various diode detectors are found in []. Because the steady-state current through the detector is very small, the microstrip can simply be terminated in the standard manner.

The Mini-Circuits ZX47-40-S+ would be an excellent low-cost COTS alternative.

%\printbibliography[heading=none, title={}, keyword={rectifier}]

\PRLsep{{\itshape Microfluidics: small channels, big headaches }}

We had anticipated having to perform a large number of tests for optimization of the impulse. Automating tests also has the advantage of removing operator bias, and (in our case) minimizing artifacts from the sample holder. Since all the components were already computer-controlled, it seemed little extra effort.

We originally planned on using techniques from the rapidly accelerating field of centrifugal microfluidics, using a broadband patch antenna smaller than the cuvette, and measuring transmission through the cuvette.

Centrifugal microfluidics has the advantage of getting a pump for free; mixing can be effected by generating vortexes by accelerating and decelerating quickly; and because everything is circular, it is easier to design equidistant.

The most important feature is the consistent "down" vector; because capillary forces 

However, aligning seemed liable to produce artifacts; runout in the spindle;

Sterilization is often effected by cytotoxic gas []. UV we resorted to autoclaving, warping.

Th edges are charred; however, we have not found any discussion of toxicity of the laser cut edges, so we assume they're fine.

In a crude version of transmission welding. Tx welding usually relies on one material being transparent, and the other opaque - clear and black plastics, for instance. We obtained nearly useable results by scuffing one surface and rubbing in fine graphite powder.

Both the hydrophobicity / wetting angle of the substrate (useful for valves with a certain threshold pressure, among other things), the adhesive surface energy, and sterilization can all be effected by UVC exposure. Unfortunately, we were not confident in the homogeneity of the 

Not all plastics can be laser welded.

3DuF; this is an excellent program 

The final process was as follows:

Just using a single-sided tape over micromachined channels didn't work for us; the tape remains sticky and stuck to the bottom of the channel, blocking it.

\begin{itemize}
	\item 1/16" 003 size Viton O-rings McMaster-Carr \#9464K103, 
	\item 3M 467MP 0.051 mm double-sided adhesive transfer tape with 200MP acrylic adhesive, DigiKey 3M9726-ND.
	Various other tapes were tried, such as 9495MP; the laser was not powerful enough to cut these.
	While the intermittent temperature rating is over 121 C, the high-pressure steam environment does seem to degrade any exposed regions of tape.
	
	A CO2 laser is usually used to cut these otherwise transparent materials. We only had a diode laser. However, the front and back paper liners absorb sufficient laser power to melt the tape between. This produces horrible results, but was sufficient for this purpose. With our 2.5 W, ~0.15 mm spot size, 450 mm/min for the tape.
	
	\item MG Chemicals 416-T Laser Printer Transparency Film, 0.1 mm thick. Presumably a PET/Mylar material.
	
	\item A vinyl cutter was used to cut the openings in the top mylar cover slip.
	\item Frame machined from polycarbonate with a 1/16" two-flute carbide endmill, 24000 RPM, between 500 and 1000 mm/min, up to 1.5 mm step-down. G-code generated with MeshCAM. This seems to withstand the autoclave without any damage.
	\item Note: the tape preferentially sticks to the back liner, rather than the front.
	With both adhesive liners on, rub the thing hard with a rounded edge and rolling pin.
	Aluminum foil tape backing on the adhesive layer.
	Don't de-weed yet. 

\end{itemize}

Note that cutting many of these materials with a laser is a bad idea. The residue will 

\begin{itemize}
	\item Tape mylar to a cardstock backing with masking tape on the sides. Cut mylar on plotter with InkCut. 175 g force. 
	\item Apply aluminum foil tape to the rear backing (with "3M" text) of the adhesive transfer tape. This supports the cut structures, without being cut itself.
	\item Stick the adhesive to the laser bed with Kapton, foil-side down. It's not a good idea to use masking tape; it'll catch fire.
	\item 
\end{itemize}

Making this device ourselves was a grave mistake that potentially cost many lives. We should have used \cite{Straight}, a COTS version which we discovered halfway through. 

I'm sorry.

\paragraph{Lessons learned:}

When trying to characterize the response to some process parameters (say, laser power), iteratively trying different parameters in series can be somewhat useful, as each trial informs the next. In this instance, we would try a speed and power, unstick the material from the bed, observe the result, decide on the course of action, and repeat. However, if it is possible to try many parameters in parallel just as fast as in series, (that is, in our case, make a coupon using [] that tries all reasonable values simultaneously), it would be very dumb not to do this.

We are very dumb.

\printbibliography[title={General fluidics resources}, keyword={microfluidics}]

\printbibliography[title={Centrifugal}, keyword={centrifugal}]

\PRLsep{{\itshape aaaaa }}

One problem with the formal, academic paper format is that one starts to believe what is written, which is a death sentence for accurate reasoning. We try to avoid this by being unprofessional.

\label{para}
\ref{para}

\clearpage
%%%%%%%%%%%%%%%%%%%%%%%%%%%%%%%%%%%%%%%%%%%%%%%%%
%{\Large Microwave Musings}\\
%
%	%%%%%%%%%%%%%%%%%%%%%%%%%%%%%%%%%%%%%%%%%%%%%%%%
%	
%	\noindent\fbox{\parbox{\linewidth}{
%			Toolchain:
%			\begin{itemize}
%				\item Failed oscillator feedback-loop optimization toolchain: QUCS 0.0.20 + python-qucs + scipy's 'basinhopper'
%				\item Successful A slightly modified ngspice + ngspyce + pyEVTK
%				\item gprMax for FDTD EM simulation
%				\item KiCAD, wcalc, scikit-rf, ngspice
%			\end{itemize}
%	}}
%	%
%	
%	
%	Microwave design has a reputation for being the purview of wizards. Modern RF software packages like HFSS, Microwave Office, Agilent's ADS, and Mathworks' RF toolbox, for which; component models 
%	
%	Luckily, this project falls perfectly within the subset of microwave technologies that do not require a goatee. The vast majority of the behavior of most circuits can be accurately modelled with the very same SPICE tools as one would use at low frequencies. With judicious application of reference designs, it seems to be possible to design 
%	
%	Before about 2005, however, it seems to have been somewhat the norm to write a simple numerical code to solve the problem at hand based on underlying principles.
%	
%	We are also aided by the fact that what took a \$150,000 computing cluster a single decade ago can now be done in a few minutes by a single budget GPU.
%
%
%
many programs try to implement their own command scripting language
if the api doesn't expose fast access to the data on each timestep, then you're limited to the features that have already been implemented

\section{Timeline}

\paragraph{Comments by others}

\Acrobatmenu{GoBack}{Back}

\end{document}

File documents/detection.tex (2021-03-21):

%!TeX root = detection
\documentclass[paper.tex]{subfiles}
\begin{document}

\begin{autem}
	I hasten to note that culturing and quantifying viral titer is a completely solved problem, and is a procedure often done in kindergarten labs. The amount of time and effort we spent on this problem was completely unjustifiable. It was driven by an acute lack of competence, equipment, and the 0.8 uL volume constraints of our original poorly designed microwave setup.\\
	
	None of the techniques that we mention are even remotely novel, and we present only the barest of experiences with each.
	Indeed, the fluorescence technique that were eventually decided on is common practice for lysis detection; our use is not novel in the slightest.
\end{autem}

Most of our methodology results are tainted by two factors:

First, the fridge froze. A small "three-way" 

T4r+,

Lack of optical with

this means that small changes in volume, position, 

\section{E. coli host culturing}

\begin{figure}[H]
	\captionsetup{singlelinecheck = false, justification=justified}
	\centering
	
	\caption{
		\light{
			\\
			We've got a thing\\
			that's called\\
			{\it Radar Love}\\}
		We've got a wave\\
		in the air}
\end{figure}

Essentially the only method of determining the activity of phage is to have it infect a suitable host. Host range

Typically, this is done either in a large tube or a flat-sided optical cuvette.

Because the variation in the optical density is quite small, this poses some rather. 

A lot of the basic facts of phage, and most of the useful techniques were determined in the 1930s. 

A small vial of liquid has a much larger surface area relative to its thermal mass. sis removed, the temperature drops very rapidly; if the temperature drops outside the "physiological range" of around 33-40 C, growth is stunted \cite{effect2003}. \cite{growth1946}. I'm not sure if this was the problem I encountered, 

As a faculative aerobe, E.coli requires a concentration of oxygen to be present in the mixture for speedy replication \cite{Effect1965}; and this supply must also be kept sterile. One method to ensure this is by using a bubbler aerator; Carolina recommends an aquarium pump with cotton-ball filters. Probably Syringe filters are a good alternative.

Another method, often used in microfluidics\cite{Microfluidic}, is that of \cite{method1951}; the Manganese dioxide catalyzed decomposition of hydrogen peroxide. $MnO_2$ is readily obtained from alkaline batteries; and in this case no sterility issues are presented. However, it is not obvious how antimicrobial $H_2O_2$ vapor can be prevented from contacting the culture.

Bottles of zero air may be more effective.

In commercial fluid transfer machines, this is often resolved by HEPA filtering the input to an enclosing cabinet.

Shaking incubators, where the flasks are 

Ensuring that a great deal of headspace was present in a sealed tube (that is, culturing 2.5 mL in a 15 mL falcon tube) was sufficient for brief, low-density.

As the size of the well decreases, the Reynolds number also decreases \footnote{In fact, in the case of a circular well, it's not obvious that this is the case - the cross section decreases faster than the characteristic length}, and turbulent flow is greatly hampered.

Even slight rotation of the tube, such that the graduations 

"Chromogenic" substances \cite{Fluorogenic1991}, or the degradation of various dyes like Methylene Blue; tetrazolium dye methods;

Using 2.5 mm diameter x 3 mm high wells cut in polycarbonate and sealed with clear packing tape. However, the presence of small bubbles in the headspace of the wells prevented a consistent reading.

We tried simply adding 1 uL of culture to the microscope slide;

The 8-bit resolution and dynamic range of most cameras did not seem sufficient to discern the turbidity; and masking and correcting for 

\cite{Vision2016} use an ingenious technique. A background with sharp light-to-dark edges is used. Slicing the image into chunks only slightly larger than the object,

The 0.8 uL sample in each was not sufficient to produce a measurable change in turbidity in a 0.2 uL - or we were not experienced enough to perform the phage lysis protocol properly.

However, we were not able to make smaller volumes of culture enter the log phase.

Another very interesting technique is that of \cite{Study2003}, 

\subfile{paper_electrophoresis}

It should be noted that 

\subsection{Detect the growth of the host, and measure effects of the virus on that growth}

\subsubsection{Plaque assay}

The plaque assay for viruses has remained essentially unchanged since d'Herelle and Delbruck's era.

Advantages over broth methods are the apparently longer infective period without agitation or 

Contamination - in both directions: if you don’t wash your hands properly before working, you might end up with a thick soup of some truly horrific bacteria.

Despite poor aseptic technique, contamination was not a serious issue - perhaps 1 contaminant region per plate.

Incubating the bacterial lawn for sufficient contrast to read the plaques imposes a ~1 to 3 day delay between test and results. Each test requires several dilution tubes

\subsubsection{Protocol and observations}

\begin{toolchain}

To simplify and for higher throughput we use the drop-cast absorption protocol of \cite{Simple2018}, which uses only a single layer of 1\% agar.

150 mL water in a 250 mL beaker covered with alu foil, with stirring, and boiled in a pot of water. 1.5 grams of nutrient agar powder \footnote{Seaweed Inc, Amazon} was added to 150  until molten. A magnetic stir bar was used to ensure all was fully melted,
and then the beaker was autoclaved for 15 minutes. After cooling to 60 C for 25 minutes in a water bath on a hotplate, 20 mL of agar was poured onto [100 mm?] polystyrene plates. The plates were left to set, then dried inverted with a flamed bent copper wire spacer for air exchange at 70 C for [1 hours?].
The plates were then stored inverted in plastic bags at 4 C until use.
\footnote{How agar percentages are specified seems somewhat ambiguous to me - is the percent of the agar itself (a viscosity measure), or the nutrient-agar mix (a growth measure)?
	Weight/weight? It appears to be w/v of the whole dry powder in distilled water.}

After cooling, 1 mL of overnight culture was poured across the plate, excess drained onto the next plate, and allowed to dry for 35 minutes at room temperature.

A control plate was made with pure stock phage and autoclaved phage.

The sample was retrieved from the cuvette by carefully removing the tape backing and withdrawing 0.8 uL from the reverse side, to avoid a silicone oil bubble.

Unfortunately, this ended up being very inconsistent.

Not having a 10 uL pipette, the 0.8 uL sample of phage was diluted in 7.5 uL of sterile broth in a microplate, then all 7.5 uL was added in 2.5 uL steps to the agar.

\st{Each 0.8 uL sample was diluted in 0.2 mL of nutrient broth, a 250x dilution. If the $10^6$ pfu.}

60c to pour was I think too high - condensation was high, even after 1 hour at 37c no change.

". The dryness of the agar is very important; if too moist, the
drops will run and coalesce, if too dry, the bacteria will grow
poorly"

The plates were dried at ~70 C in an oven with the slightly open.

The plates were incubated overnight. The lawn was very nicely formed; the phage concentration was

It was difficult to tell where the drops were placed, and they ran together.

\begin{figure}[H]
	\captionsetup{singlelinecheck = false, justification=justified}
	\centering
	
\end{figure}

\end{toolchain}

\subsubsection{Broth assays}

This, however, requires a microplate reader which can simultaneously agitate for sufficient oxygen, incubate, and 

Tetrazolium dyes are metabolized 

GFP

\subsubsection{Impedance assay}

Because it would be difficult to maintain temperature on and multiplexing was difficult, low-frequency E. coli culture monitoring impedance spectra were performed separately.

An ultra-simple KHz impedance spectrometer was built, following \cite{unconventional2015}.

Purely contactless, capacitively coupled impedance measurement was found to have an unworkably small signal level;
however, a single conduction path and a single capacitive coupling through the Kapton film yielded a 10 mV signal level with 5V Vpp drive. A 110x amplifier was used to bring levels up.

0.7 mm gold-plated spring pins ('pogo' pins) pierced the silicone oil layer and pressed against the bottom tape; 1.4 mm pads were the second electrode.\footnote{Platinum, gold wire, anodized aluminum, or graphite would likely have worked equally well.} The pins were wiped with 99\% alcohol before each test.

2.5 uL stationary e. coli culture was added to 5 uL broth and 2.5 uL phage or autoclaved phage.

0 - 3 were phage; 4-7 were autoclaved phage.

Failure. decrease in signal rather than the expected increase, and no difference between autoclaved and phage.

Looking at this later - the fluid has leaked out of the wells after some time. That might be why this didn't work.

\section{E. coli flavin autofluorescence}

Added 2.5 uL to 5 uL broth. There does seem to be an fluorescence signal from; 100 uS long pulse, -70 mV is a good threshold.
Hz w/e.c, 2.9-5 Hz broth

Put the original eppendorf culture full of e. coli in. Jumped to 18 Hz @ -81 mV! Fantastic!

Thought I was all clever-like, using the oscope trigger out as the comparator and plugging that into a counter,
but above 20 Hz there's no thingy.

No. No go.

Weird background noise.

" By moving into this hydrophobic environment and away from the solvent, the ethidium cation is forced to shed any water molecules that were associated with it. As water is a highly efficient fluorescence quencher, the removal of these water molecules allows the ethidium to fluoresce.[citation needed]"

Otherwise, GFP-flouresecent strains of E. coli, or phage which has been labeled with a 

\subsection{Detect the release of intracellular material due to the lysis of the host}

One common target is the enzyme $\beta$-galactosidase. E. coli and other. Both  isopropyl $\beta$-D-thiogalactoside. Lactose itself is a reasonable substitute (Borralho \cite{Lactose2002}).

Ijzerman

X-gal \cite{Improved}

X-gal is only soluble in DMF and DMSO. We choose DMSO due to DMF's toxicity. DMSO is miscible with water, so that works out nicely. Solutions of < 0.75\% DMSO seem to not be cytotoxic.

I was introduced to this by Ijzerman \cite{liquid1993}, who recommend chlorophenol red $\beta$-D-galactopyranoside (CPRG) as the chromogen for a high sensitivity. CPRG is very hard to obtain except through Sigma.

beta-galactosidase

\begin{figure}[H]
	\captionsetup{singlelinecheck = false, justification=justified}
	\centering
	
	\caption{The very pretty opalescent blue culture caused by E. coli B trying to metabolize lactose in an X-gal $\beta$-galactosidase enzyme indicator.}
\end{figure}



 It’s probably in principle possible to synthesize them yourself, but it’s totally impractical. You will probably need a corporate address HS codes. 

T4 has a comparatively huge genome, which makes this easier.

\subsection{Detect the lysis of the virus, and the release of intra-viral material}

A fingerprint, for instance, has only about 0.2 ng of DNA (Subhani), so contamination is not a huge issue.

Phages release several small compounds like putrescine and spermadine when broken (Minagawa\cite{characteristics1961}). These can be indicated colorimetrically at ppm scales with ninhydrin, or at nanogram scales via fluorescamine. 

Biotium Gelgreen has a very specific advantage: to increase the safety of the dye, the flurophore is tied to some huge proprietary molecule, preventing it from diffusing through membranes or capsids. This has the side effect of making the fluorescence intensity strictly related to the quantity of genomic material dispersed in the solvent, rather than 

\subsubsection{Nucleic acid UV extinction }

The 260 nm extinction due to 60 MDa DNA at concentration $10^8 = 10e-9$. With a 1 mm path length is 0.002x. that's going to be swamped by everything else.

\subsection{Directly detect the virus itself}

PEG apparently concentrates to $10^{12}$ or 13 no matter what the starting concentration is (huh?), very convenient.

Early workers on phage mention\cite{ADSORPTION1940}  that cultures with a titer above about $10^10$ have an opalescent blue tint due to Tyndall scattering. Schlesinger in 1933 \cite{Beobachtung1933} (paper is in German). This technique appears to have been forgotten?

Concentrated can be put into the microgram range of high-sensitivity protein assays like BCA or Bradford, but that requires propagation and PEG precipitation, plus many such assays pose disposal hazards and stain labware. 

\end{document}

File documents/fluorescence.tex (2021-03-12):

%!TeX root = fluorescence
\documentclass[paper.tex]{subfiles}
\begin{document}

\begin{figure}[H]
	\captionsetup{singlelinecheck = false, justification=justified}
	\centering
	
	\caption{}
\end{figure}

\begin{figure}[H]
	\captionsetup{singlelinecheck = false, justification=justified}
	\centering
	
	\caption{}
\end{figure}

the base had integral overcurrent protection, which was triggered a few times during development - a very useful 

For one thing, GelGreen appears to be eminiently stable - samples can be stored for long periods of time; pre-mixed batches. 

Unlike luminescence techniques, 

%\subsubsection{Light source}

A modulation frequency of 

Lexan fluro was unex

Acridine orange (N-alkylacridinium)

Orange 16 

Fluoris
 
 LOL
 
(apologies to Floris Laporte)

sketches of light source in inkscape

from [], using ImageJ to stack. works great on cheap cmos cameras - interestingly doesn't work at all on more expensive cameras. - 
almost good enough - great for diagnostics

interestingly, the fact that the camera has color is quite valuable; filtering the green out can increase sensitivity a lot

a 30-s exposure on a cheap camera also almost got there.

Should make a discord as lab notebook

virus-specific

hemagglutinin test

the microscope is largely unnecessary. 

bleaching was not obviously an issue, nor was storage with the dye bound to DNA.

A white LED with a high color-rendering index (DK) seemed to have more power in the blue passband; however, green leakage around the filter was too strong. 

Unlike gels or plastic-glass sandwiches as used by Tiffen, thin-film filters have the disadvantage that the pass-band depends greatly on the angle of incidence.  

$$\lambda = \lambda \sqrt{1-sin(\theta)^2}$$

The wavelength shifts shorter (bluer) as $\theta$ increases.

This isn't an issue for the excitation filter, but is an issue for the.

Since the LEDs and flurophore emissions are not naturally collimated, this poses a little bit of an issue.
The microscope objective seems to provide sufficient collimation for the emission filter.

The Edmund filter was unmounted glass. Also, these thin-film filters do not extend to the edge of the glass. Edge-blankening ("inked") fil

The LED was about 3 cm away, and put through a ~3 mm aperture in a piece of PVC pipe. The output from the filter was directly into the 1 mm fiber, itself improving the bandpass.

The 10 nm FWHM emission filter is much narrower than professional GFP filters, especially the super-wide edge-pass ones; a lot of photons are lost that way. However, it's still more than sufficient. 

it has been noted that water is a good fluorescence quencher and that this might be how 

If time-domain filtering is sufficient, 

Low background is required.

Xu's method \cite{Quantification2020}

Performance of this arrangement was very satisfactory. A 10-second integration time, with, produced a background fluorescence signal of ~1500 counts, with per-sample stability of approximately $\pm 1500$ counts. The  

Contrary to standard microscopy, you want as little excitation light to enter the objective as possible. Using the existing 

autofluroescneces Lexan

Nanodrop, using 280 nm absorbance. They're also \$10,000.

the input edge is considered a clock; the minimum pulse width limits apply, but are not clearly specified in the datasheet. In this case (1/155 mhz) = 6 ns.

However, we had no luck with precipitation.

Luckily, a recent paper has the answer: direct fluorescent detection of DNA in solution, outside using dyes that bind to (intercalate into) DNA. GelGreen doesn’t penetrate.

As noted by [xi?], this is a saturating effect; if too many flurophores intercalate into the DNA the fluorescence is weaker. A “1/4000” solution of GG in distilled water mixed 50/50 with the sample (“1/8000”) worked great in our case.

(Phi6 uses an RNA - many dyes have different responses to single-stranded (ss)DNA, dsDNA, or 

autof

With the setup we’re using and the small quantities, the excitation light is somewhere around ~$10^5$ times as powerful as the emission. This doesn’t seem to be a big issue gel-docs, picking out bands on gels - they don’t usually seem to use excitation filters; however, to get the excitation bleed-through low enough to do this quantitative assay, the bleed-through must be really low, and in our testing proper dielectric filters are required on both the excitation and emission sides. 

There are a few sources of noise:

PMT dark counts
Some be filtered out by judicious use of comparator pulse height threshold, the lock-in takes care of it. A non-issue in our case.
Ambient light leakage
Using microscope optics and the lock-in, essentially a non-issue for use, surprisingly. Some fluorescence microscopes use micron-size apertures to limit the depth of field to avoid Putting 
Figure out the average current limit for your PMT, the expected voltage based on your load resistor value and watch that it never exceeds it. It’ll be fine. Even with the room lights

Note that PMTs are happy to endure very high pulse currents, like flashbulbs for exciting; no shutters or anything required. Gating the photomultiplier HV is another technique.

The PMT was at maximum sensitivity (in fact, slightly above max voltage)

Gel-docs , with spectra specified using the Wratten scale. These filters alone do not seem to have optical density (OD - logarithmic value of transmission in the blocking band) values sufficient for this qfluor. 

Most commercial microscopes use dichroic beamsplitters, allowing the excitation and emission beam to go through the same objective. The dichroic only removes the excitation to the 1\% level - you still need the dielectric filters, and they’re really expensive. With fiber optic excitation at right angles to the objective, excitation scattering was low enough that the dichroic was unnecessary. 

The fiber optic \cite{vurek1982nanoliter}

You might be wondering why the filters are even required - why not just subtract the excitation bleed-through with a control? Unfortunately, any miniscule variation in the scattering of the excitation will be orders of magnitude larger than the fluorescence signal you’re looking for.

Some papers discuss adding a third chopper or gate period or photomultiplier or to measure the drift of the excitation light source.

PCR is another method

Silicon photomultipliers like ON's C-Series are almost certainly sufficient for this application, eliminating the HV requirements of PMTs at the cost of a smaller active area.

half-life is 0.693 times the average lifetime. 

I thought the pulse height

An even better Phase-shift time domain fluorimetry. Iwata use a 20 MHz DSO to measure a 5 ns $\tau$ fluorophore. However, this involves a light source with a fast modulation bandwidth; and in the implementation they describe, the PMT must be in the voltage mode.

Called time-correlated photon counting.

Another neat technique is to add I/Q

Then your 

Cree recommends staying below 300\% of the continuous power when modulating an LED.

While there are ways to deconvolve a slow falling edge, there’s another problem: per time interval, the time spent in the excitation-off, flurophore exponential decay time is proportional to the frequency of the excitation light. If you’re only getting 1000 photons from the sample per second, the dye lifetime is 5 ns, and you’re turning the light on and off at 1 MHz, you’re only getting a [] photons from the exponential decay region. Even with a long exposure, that doesn’t seem to be enough to pick up the decay. 

Another way to pick up this phase shift is to make your lock-in amplifier phase-sensitive - very simple (a 2x clock put into a flip-flop divider, then the middle). This also wasn’t nearly good enough, completely useless. 

Simple spectrally-filtered intensity is good enough.

Contrary to luminescence, you have control over when the excitation and emission light turns on, so you can do a lock-in. This doesn’t subtract the excitation bleed-through, but it 

Polarization is a neat way to filter; linearly polarize the excitation, the emission comes out whatever orientation the DNA happens to be, which is usually random. Apparently

Relaxation times of acrynylomadfnium dyes extend from a few picoseconds up to once the complex is produced. This is a saturable, hormetic effect; if all the binding sites are filled on the DNA the intensity is quenched, as noted by Xie. 

\end{document}

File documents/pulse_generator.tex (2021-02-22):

%!TeX root = pulse_generator
\documentclass[paper.tex]{subfiles}
\begin{document}

Spark gaps 

\cite{kHz1995} uses an interesting construction of a pressurized spark gap.

The ZTX417 parts are expensive (\$15 apiece, as of this writing). 

[] mention triggering parameters

There seem to be two main designs: 

drivers Pockels cells for Q switching.

Schaal patent  which can produce 70 ps edges using less expensive ZTX415 (although the all-important RF "second schematic", the ).

marx or marx-free

Almost   Diagnostics of such pulses are difficult.

Attenuators that are rated for such high peak powers are hard to find.

Oak \cite{fast1991} Figure 1 offers a circuit to evaluate avalanche behavior of transistors. Using this, the 

Based on the coplanar heating cnannel of \cite{Microwave2007}.

Impedance matching to appears to be a solved problem. \cite{Microchamber2011} provide a good review, and offer a design using a high-impedance exposure cell in parallel with a 50 ohm resistor, which offers excellent performance to at least 1 GHz. Attenuator for diagnostics are also built in. This cell should be used rather than our design. \cite{Characterization2012}

\end{document}

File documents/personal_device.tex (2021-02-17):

%!TeX root = personal_device
\documentclass[paper.tex]{subfiles}
\begin{document}
%
%\begin{autem}
%What follows is intended to be a casual, first-principles e. Be very careful with its conclusions.
%\end{autem}
%
%{\color{red} speculation \{ } 
%
%%\clearpage
{\Large \it The plausibility of low-cost microwave masks}\\

With the most recent few generations of semiconductor processes, producing significant powers in the X-band has become inexpensive. Silicon transistors are limited in their output power and gain; Silicon-on-insulator topologies 

This is perhaps most readily illustrated with the commercial HB100 radar module. This device implements a complete Doppler radar with two RF FETs and one dielectric resonator on a standard FR4 substrate. It operates at 10.6 GHz, yet are produced for under \$3.

Our crude experimentation has yielded about 10 mW with a single SiGe:C transistor, the Infineon BFP620 (\$ 0.34 apiece \@ 1000-of.). For the personal microwave sterilizer, given the threshold levels found by Yang, this corresponds to a cost per sterilized cubic centimeter of approx. \cite{BFP620H7764XTSA1}.

Trivially extending great work by \cite{Focusing} on passive reflectarrays, a 40-element active-antenna phased array, each element of which consists of a negative-resistance device such as the BFP620 transistor, a tuning varactor, a patch antenna, and a resonator, each contributing a pulsed tone of 500 nanoseconds length and 10 milliwatts of RF power, and a focal point spatial scan rate and pulse repetition frequency of 6 KHz. produces a field pattern which, when scanned, appears to be suitable to deny respiratory transmission in a 'face shield' configuration. 

Such a field would comply with all standards by at least a factor of 20.

%figure from ipynb

\begin{figure}[H]
	\captionsetup{singlelinecheck = false, justification=justified}
	\centering
	
	\caption{\\ How simple an active antenna element can be. This is based on the feedback-loop oscillator of \cite{SmallSize2008}, and uses a single CEL CE3520K3 GaAs FET (\$2.5) and one 100pF capacitor. It oscillated with extreme instability at about 5 GHz.}
\end{figure}

\begin{figure}[H]
	\captionsetup{singlelinecheck = false, justification=justified}
	\centering
	
	\caption{\\ A wideband tunable 7 GHz VCO based on \cite{TripleTuned2008}. This uses an Infineon BFP620 SiGe:C transistor (\$0.3) and a network of four varactor diodes. Unfortunately, the Si varactors did not appear to have a sufficiently high Q to prevent mode-hopping, and the output spectrum reflects the ignorance of its designer; however, it appeared to be capable of producing the 10 dBm required above.}
\end{figure}

\begin{figure}[H]
	\captionsetup{singlelinecheck = false, justification=justified}
	\centering
	\includesvg[width=\textwidth]{personal_device_E}
	\caption{Near-field focused phased array}
\end{figure}

% a prototype oscillator

Injection locking rather than discrete phase shifters saves a number of components.

Such a device would cost about \$12 in silicon at prototype prices, provide half a month of battery life on two alkaline AAA cells, 

We demonstrate this form factor because, superficially, there are fewer people than there are places. But is such a device really necessary or useful? Is it sufficiently superior to a fiber mask to justify spending energy developing it? It has the advantage of being self-cleaning; and hair, eyes; a hand brought near the face is immediately sterilized.

On the other hand, a personal device may present issues with participation and production volume. 

Interference

If HFSS or ADS are not available, coupled SPICE-FDTD methods appear to be particularly simple and effective for these types of problems.

The advantage of the phased array is in the free-space power combining and the near-field focusing.

In our crude experiments, the loss tangent and poor impedance control of inexpensive substrates did not appear to pose a problem in itself; standard FR-4 or even PET substrate and screen-printed metal techniques seen in high-volume RFID tag production may be of some use. 

However, the Q factor of tuning elements on such lossy materials appears to be too high to form useful oscillators. Air-dielectric coaxial, Barium titanate dielectric slab resonators, or various types of substrate-independent resonators may all be suitable for this purpose.

{\color{red} \} speculation } 

%\end{multicols}

%\clearpage
%%%%%%%%%%%%%%%%%%%%%%%%%%%%%%%%%%%%%%%%%%%%%%%%
%{\Large Interference}\\
%\begin{multicols}{1}
%%%%%%%%%%%%%%%%%%%%%%%%%%%%%%%%%%%%%%%%%%%%%%%%

%
%%%%%%%%%%%%%%%%%%%%%%%%%%%%%%%%%%%%%%%%%%%%%%%%%
%{\Large Mass production}
%%%%%%%%%%%%%%%%%%%%%%%%%%%%%%%%%%%%%%%%%%%%%%%%%
%
%
%
%Almost all components on the device can be replicated with fully vertically-integrated first-principles. Capacitors can be
%
%If this 'electromagnetic mask' form is the ideal (not nearly), 
%
%The largest RFID plants can produce
%
%a minimum of 5 GaAs or SiGe:C transistors will be required. Without SOI or, it does not appear that 
%
%As a lower bound, there are 1 million hospital beds in the U.S. [AHA 2018]; and as an upper bound obtaining global herd immunity would take 1.75 billion units.
%
%It is difficult to determine the supply capacity for these semiconductor processes; information is not forthcoming from the manufacturers. Fermi estimates \footnote{GaAs MMIC market of \$2.2 Bn USD / random sample of MMIC prices = about 2 Bil devices / yr, 3e9 wifi connected devices produced each year,}
%
%
%
%It is possible to use common Si-based devices at these frequencies, especially with second-harmonic techniques [Winch 1982]. However, obtaining the required gain and output power is not a trivial matter. 
%
%The techniques and equipment required to produce these devices are extremely complex; load-lock UHV,  
%
%
%Figures are not forthcoming, 
%
%Given the supply difficulties of comparatively simple materials such as Tyvek at pandemic scales, it is difficult to imagine that RF semiconductor production can be immediately re-tasked and scaled to this degree. 
%
%\paragraph{\textbf{Vacuum RF triode}}\
%
%
%
%Especially combined with an integrated titanium sorption pump,
%
%One concern is the large filament heater power, which prevents the use of low-cost button cells for power. Use of cold-cathode field-emitter arrays would alleviate this issue, but at the cost of complexity.
%
%Small tungsten incandescent lights are available down to 0.05 watts. With a suitable high-efficiency cathode coating, a pulsed heater power of less than 0.02
%
%
%
%\end{multicols}
%
%
%The X-band is also minimally absorbed by air, allowing action in the far-field and scaling to square-kilometer areas with single installations.
%
%
%
%
%\clearpage
%

\end{document}

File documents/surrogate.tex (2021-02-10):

%!TeX root = surrogate
\documentclass[paper.tex]{subfiles}
\begin{document}
	
%Biosafety labs often have lesser requirements for primary samples; if 

\begin{fquote}[ Kellenberger][\cite{History1995}] 
	Only somebody who has experimentally worked with his own hands on various other systems can fully appreciate the fundamental change brought by phage.
\end{fquote}

\end{document}

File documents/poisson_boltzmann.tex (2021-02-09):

%!TeX root = poisson_boltzmann
\documentclass[paper.tex]{subfiles}
\begin{document}

\begin{autem}
	TODO: Fix this up. This is a central point that should have been done a long time ago. 
\end{autem}

Poisson-Boltzmann family of equations is an extension of standard Laplace and Poisson potentials to solutions containing ions. It considers an equilibrium. As with all models, there are many nuances to using these correctly; whether various approximations hold, etc. We will ignore all subtleties for now.. 

\textit{Sparselizard} has built-in support for membranes and stokes drag, and might be a good next step. Almost all finite-element programs require PB to be input in weak form, which is pretty tricky. Sympde can help with the weak form. Medusa allows input in strong form, which is convenient.

Mathematica has great support for FEM, but seems to choke on the nonlinear Poisson-Boltzmann for some reason. 

DelPhi poisson-boltzmann solver versions before 6.0 support spherical geometric objects, but flatly refuse to solve a problem this big. A few other solvers exist but are more suited for.

Božič \cite{How2012} consider an empty capsid.

The generalized Poisson equation is 

$$\nabla \cdot \left(\epsilon\ \nabla \bar\phi \right) = - \rho$$

We shamelessly steal Brackley \cite{Electrostatic2020}'s formulation (thanks for such detail!) with one exception. Most solutions consider an equilibrium. However, we are specifically designing the pulse to be too short for ion equilibriation to occur. Therefore we solve in two steps: First the Poisson-Boltzmann equation is run to determine the charge density due to screening.

Reproducing here for convenience:

$$\nabla \cdot \left(\epsilon\ \nabla \bar\phi \right) - \epsilon \kappa^2 \sinh(\bar\phi) = - \rho$$ 

is the potential in V, kappa is a Debye-Huckel parameter. They use an internal dielectric constant of 5, an external of 80 ($\epsilon =  80\epsilon_0$). 1/10 k1

$$\hat\phi = \frac{e_0 \phi}{}$$

where $e_0$ is the electron charge, $k_b$ the Boltzmann constant, and 

Brackley provide a very convenient analytical solution to the potential in the solvated two-shell case. With \cite{Deformation1991} \cite{Electrostatic2013}.

With the 

DO A LIST OF PROGRAMS LIKE BEFORE

\end{document}

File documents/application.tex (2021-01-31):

%!TeX root = application
\documentclass[paper.tex]{subfiles}
\begin{document}

Free-space "vaccination" of people or spaces is all well and good; but a treatment would seem to be superior. Far fewer installations would be required, cost would be of less object, and effectiveness would not depend on widespread public acceptance. Safety concerns due to continuous exposures would also be lessened.

Assume that the virus has a resonant frequency about 100 V/m. 

And so, is it possible to non-invasively produce this effect deep within infected tissue - to break every capsid in the body wholesale?

 Applying microwave power to the body is already used extensively in diathermy (the internal heating of tissue for therapeutic effect) and hyperthermy (the overheating or cauterization of tissue for destructive effect). While most diathermy systems use much lower frequencies for deeper penetration, several papers have explored the 10 GHz band. 
 
 Industry Canada only appears to offer an instantaneous limit at $1.35 \times 10^-4$.
 
 6 cm of l
 
 The 
 
 Fat and 
 
 The penetration of microwave power is very sensitive to 
 
 Conduction effects. Because the transmission line voltage only goes as the to the square root of the input power
 
 There seems to be some sort of focusing effect which makes internal bronchoscopic treatment slightly more effective than might be expected.

There is much historical precedent for applying microwave power to the body diathermy (the internal heating of tissue for therapeutic effect) and hyperthermy (the overheating or cauterization of tissue for destructive effect). 

While the majority of diathermy systems use much lower frequencies for deeper heating penetration, several papers have explored the 10 GHz band, almost exclusively for superficial hyperthermia.

NCoV has a unique appreciation for nervous system \cite{neuroinvasive2020}, and SARS is usually found widely distributed throughout many of the most well-regarded organs \cite{Organ2004}, shielded by an average of 4 cm of chest wall [Schroeder 2013]. 

However, it would be an understatement to say that destruction of lung tissue is significant in the lethality of SARS [Nicholls 2006], \cite{situ2020}; largely the lung type II alveolar cells 

A bronchoscopic technique may therefore be effective, very similarly to that demonstrated by [Yuan 2019]: in adults, the bronchi are less than 2 mm thick [Theriault 2018] and the lungs themselves are only on the order of 7 mm thick [Chekan 2016]. The main bronchus is about 8 mm in diameter.

High microwave frequencies are very strongly attenuated by tissue. However, we have a large amount of margin in the electric field - 4 orders of magnitude - that we can trade for penetration depth.

Industry Canada limits on the instantaneous electric field anywhere inside the body are $1.35 \times 10^{-4}$ V/m $\times$ Hz (\cite{RSS1022015}, Table 4) - that is, $0.81 \times 10^6$ V/m @ 6 GHz to $1.2 \times 10^6$ V/m @ 9 GHz. It should be noted that more recent standards have abandoned instantaneous electric field limits altogether, asserting that they have little biological rationale (\cite{C95}, B.4.3, {\it Rationale for pulsed RF field limits}).\footnotemark

In addition to these limits, the "microwave hearing threshold" - the pulse energy density threshold at which the slightest nerve stimulation begins to occur, should also be respected. In fact, ultra-high pnerve stimulation has been 

It is difficult to intuit how 40,000 watts can possibly be safe. It's useful to note, however, that the total energy dissipated in each pulse is . An oft-cited figure for the energy in a whisper is 10 mJ; while no clinical data are available, whispering at someone is rarely considered calamitous\citationneeded!

Laser treatments can exceed hundreds of megawatts.

 Thermoacoustic effects should also be considered.

\footnotetext{It should also be noted that at very specific pulsed regimes at millimeter wavelengths (far beyond our study) mere adherence to the letter of the law may not be sufficient for protection\cite{Limitations}.}

Considering only the electric field skin depth\footnotemark\cite{Safety2001}\cite{Physical1982} of average lung tissue\cite{gabriel1996compilation}\cite{Dielectricb}\cite{Dielectric}\cite{Tissue2018} (which changes considerably based on inflation), at 8 GHz it appears to be possible to achieve the required field of 150 V/m at a very reasonable depth of 60 mm. 

We could not find any data on the distribution of gas exchange throughout the cross-section of the lung.

Two complications present themselves. An annoying layer of muscle 

From cursory simulations, it seems quite difficult to generate such high electric fields with a small dipole antenna in the bronchi unless almost implausibly high powers are input. On the other hand, well-tuned. Second, these results are sensitive to the precise

\footnotetext{In our case, it seems to make the most sense to discuss the attenuation of the electric field, V/m, rather than the field power (also referred to as the {\it intensity}),\Wsqm, since the inactivation seems most closely related to the former. Strictly speaking, penetration depth refers to the depth at which the power is reduced by 1/$e$; skin depth, where the electric field is 1/$e$. The penetration depth is simply half the skin depth.\cite{Penetration2019a} If we refer to penetration depth without making this distinction explicit, we are referring to the electric field penetration depth.}

Conduction effects. Because the transmission line voltage only goes as the square root of the input power

There seems to be some sort of focusing effect which makes internal bronchoscopic treatment slightly more effective than might be expected.

While such waveguide applicators provide excellent efficiency, at these frequency ranges the area of high field is quite tightly concentrated and may not be 

The 8 GHz tone does not necessarily need to be the fundamental. A carrier wave with a more deeply penetrating wavelength could be used. 

If the carrier is lower in frequency, non-linear materials\cite{Theory1973} will be needed for harmonic generation, or implantable resonators and re-radiators. There are a few paramagnetic contrast agents used in MRI that might be useful for this if the efficiency is sufficient. If the carrier is higher, it can simply be modulated with an 8 GHz tone. In the latter case, there are so-called 'optical windows' in the absorption spectra of tissues, particularly in the near-IR range; however, none seem sufficiently transparent to be useful.

My kingdom for a Bragg peak!

\clearpage
\printbibliography[heading=none, title={}, keyword={standards}]

\end{document}

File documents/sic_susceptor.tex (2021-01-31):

%!TeX root = sic_susceptor
\documentclass[paper.tex]{subfiles}
\begin{document}

\section{Silicon carbide test}

To verify that we can detect a resonance with this setup, we use a microwave susceptor mixture described by \cite{Effect2016}, which can be tuned to the correct range by varying the concentration of SiC to binder. We used the S-1 mixture.

0.6g 2000-mesh silicon carbide powder was added to 1.4 g white Elmer's glue, mixed manually until homogeneous,
 applied to a Mylar film, and dried with a hair dryer. A small wafer of the hardened mixture, perhaps 0.3 mm thick, 5 mm x 2 mm, was placed directly on top of the coplanar waveguide.

The spectrum was then captured, averaging multiple sweeps of the VCO. A background spectrum was taken without the wafer in place, and then the two sweeps were subtracted.

\begin{figure}[H]
	\includesvg[width=\textwidth]{../firmware/eppenwolf/runs/sic_susceptor/sic_9_3}
 	\caption{}
\end{figure}

\begin{figure}[H]
	\includesvg[width=\textwidth]{../firmware/eppenwolf/runs/sic_susceptor/sic_9_2}
 	\caption{}
\end{figure}

\cite{Effect2016} measures a peak at about 7.2 GHz. Our peak is at approximately $7.84 \pm \approx 0.25$ GHz, which is well within variation in powder grain sizes and concentration.

The paper specifies the reflection loss, S$_{11}$. Unfortunately, having not designed in directional couplers, it is probably not possible to directly determine S$_{21}$ and S$_{11}$ with this setup.

Naively, we might expect the peak to appear as a decrease at both sensors; instead it appears as an increase in the far sensor and decrease in the near sensor. It could be possible that the presence of the dielectric wafer has merely detuned an existing resonance, that the peak is a coincidence, and that these data mean nothing.

%$\strike $
The raw voltage plots do not suggest that this is the case; but it is nonetheless concerning.

\footnote{The paper mentions that the "blending fraction of silicon carbide powders to epoxy resin was 30 \%, 35 \%, 40 \%, 45 \% and 50\% by weight". That seems a little ambiguous as to whether that's "weight per total mass" or "weight per epoxy".}

\end{document}

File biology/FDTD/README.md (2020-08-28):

Duke

10.13099/ViP-Duke-V2.0  

V2.0.1

Duke

"Each voxel model (.raw) comes with an associated descriptor file (.txt). In this file, the first column gives a unique index for each tissue. Columns 2 to 4 are color codes for the tissues in SEMCAD X and Sim4Life. The last column shows the tissue name. The number and size of the voxels along each direction (x,y,z) is given at the end of the document."

Christ A, Kainz W, Hahn E G, Honegger K, Zefferer M, Neufeld E, Rascher W, Janka R, Bautz W, Chen J, Kiefer B, Schmitt P, Hollenbach H P, Shen J, Oberle M, Szczerba D, Kam A, Guag J W, and Kuster N, The Virtual Family - development of surface-based anatomical models of two adults and two children for dosimetric simulations, Physics in Medicine and Biology, 55(2):N23-N38, 2010.

itis.swiss/vip

chunks:

_4.raw:

Origin:
-190
240
-260

The material .txt file generated has the format

> id (r g b color) name.

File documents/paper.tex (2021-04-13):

\documentclass[fleqn,10pt]{article}

\include{preamble}

\begin{document}

\subfile{title}

\tableofcontents

\section{Figures which have little to do with our conclusion but are pretty nonetheless}

\begin{figure}[H]
	\captionsetup{singlelinecheck = false, justification=justified}
	\centering
	
	\caption{\\ \textit{Chengxiang} nanosecond pulse exposure jig. Pulser seen off the left. Pulse shaping plate not shown. Aluminum disc belongs to the scan-conversion digitizer, not used in this study.}
\end{figure}
	
\begin{figure}[H]
	\captionsetup{singlelinecheck = false, justification=justified}
	\centering
	
	\caption{\\ \textit{Eppenwolf} misguided pulsed X-Band microwave spectrometer used in this study. (cuvette shown was replaced by the same )}
\end{figure}

\begin{figure}[H]
	\captionsetup{singlelinecheck = false, justification=justified}
	\centering
	
	\caption{Simulation of a (largely ineffective) bronchoscopic method.}
\end{figure}

\begin{figure}[H]
	\captionsetup{singlelinecheck = false, justification=justified}
	\centering
	
	\caption{FDTD simulation geometry of the 0.3 mm coplanar waveguide exposure cell. Red object is the fluid channel. Visualized with Paraview.
		\ghfile{covidinator/electronics/simple_fdtd/run/microfluidic_coplanar.py}}
\end{figure}

\begin{figure}[H]
	%	\makebox[\textwidth][c]{
	\includesvg[width=\textwidth]{propagated_waveforms}
	\caption{Brillouin precursor propagation through tissue (reproduced from section 6).\\
	(a) Gaussian monopulse with 16 ps FWHM.\\
	(b) Optimized 10 GHz sawtooth wave. Note the slight high-frequency ripple.\\ This has a frequency of approximately 1.5 GHz.\\
	(c) Prototypical precursor 10 GHz sine burst.\\
	(d) Continuous 10 GHz sine tone.}
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

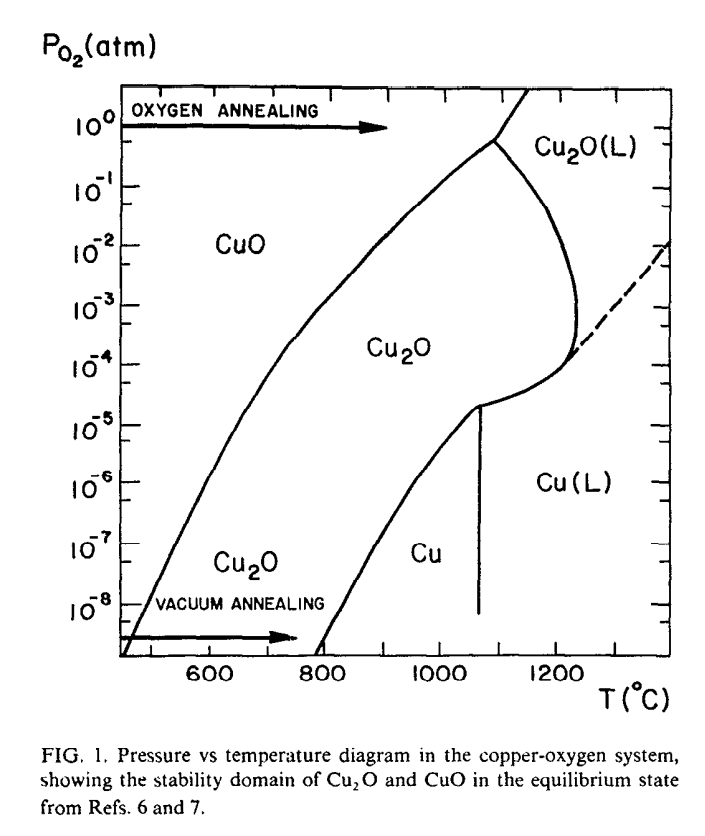
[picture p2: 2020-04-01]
media/Screenshot from 2020-03-31 14-09-16.png

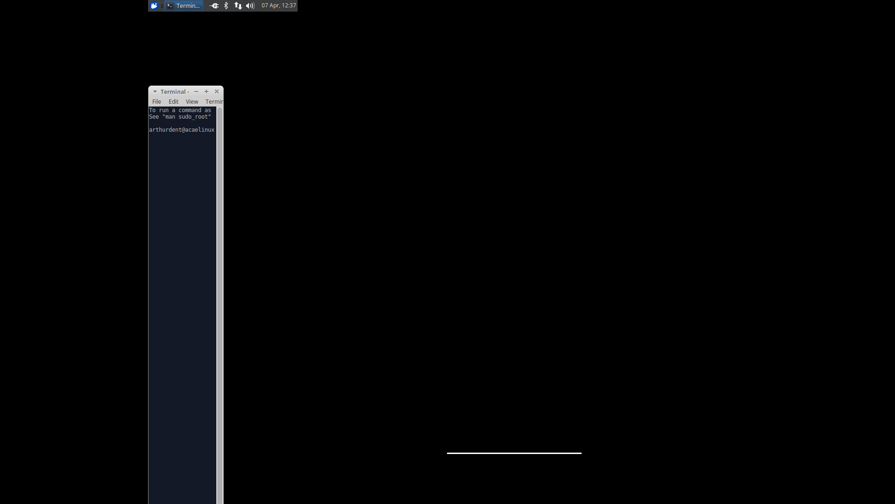
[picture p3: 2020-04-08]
media/Screenshot from 2020-04-07 12-37-25.png

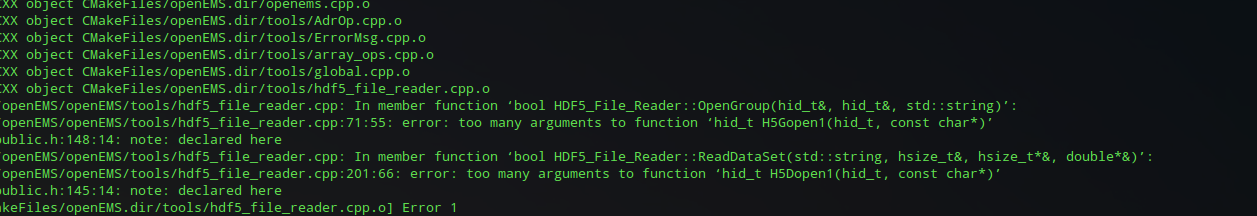
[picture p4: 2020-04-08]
media/Screenshot from 2020-04-07 23-54-45.png

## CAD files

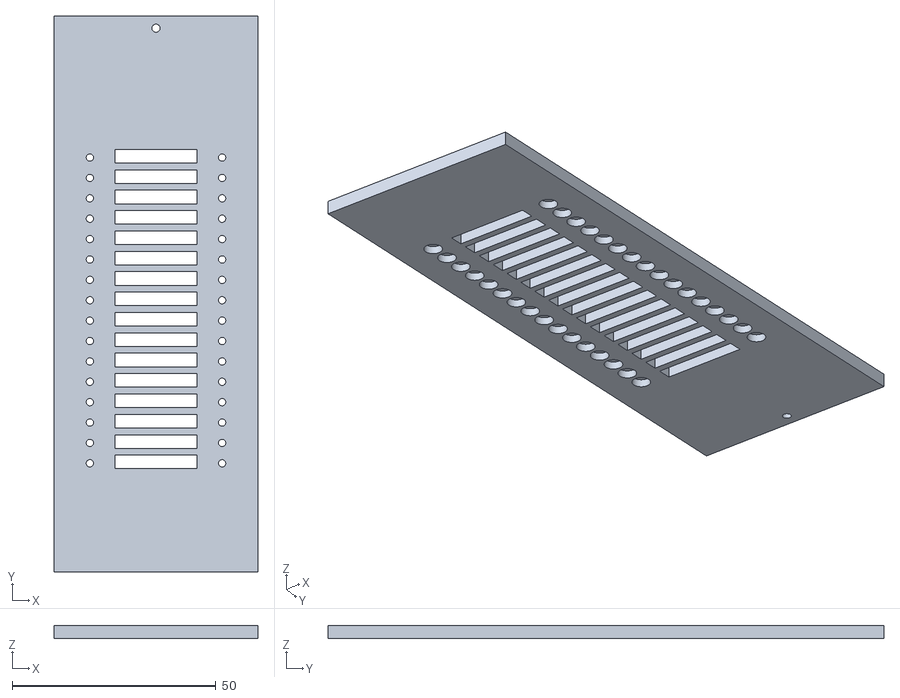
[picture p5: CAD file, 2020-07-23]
mechanical/microfluidic/slide_id_1/frame.stl
50.0 x 136.4 x 3.17

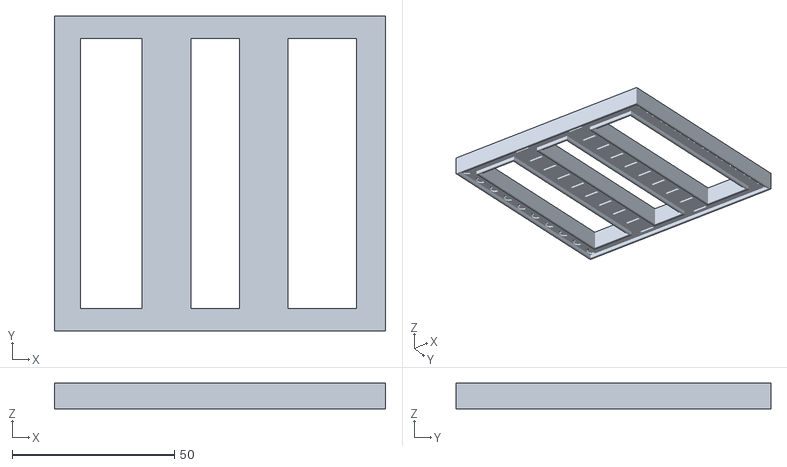
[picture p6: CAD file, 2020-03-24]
mechanical/mk1-5_furnace/insulator.stl
102.0 x 97.0 x 8.00

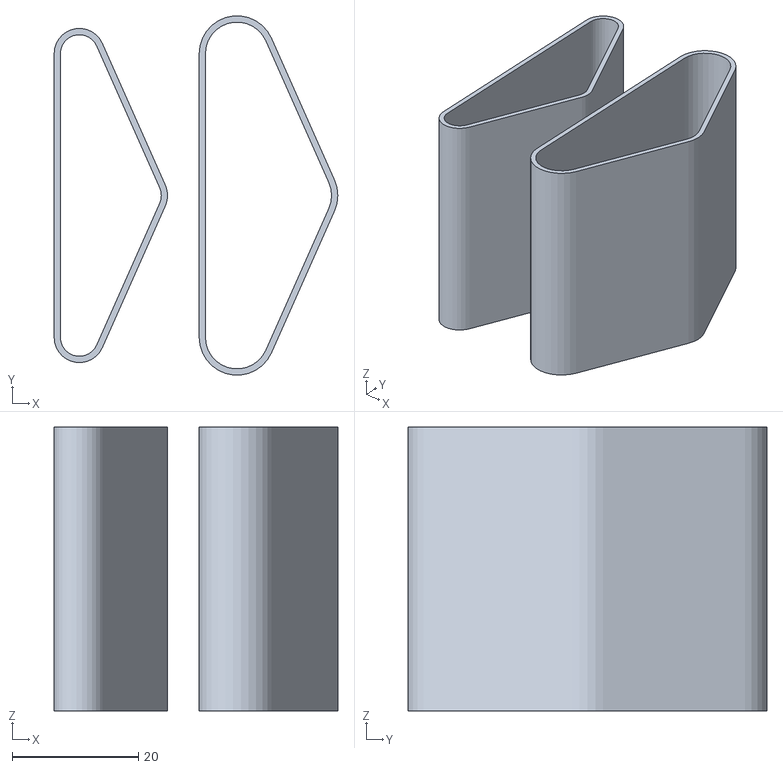
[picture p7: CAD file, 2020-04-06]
mechanical/Mk2-2_furnace/mechanical/MLI.stl
45.0 x 56.9 x 45.0

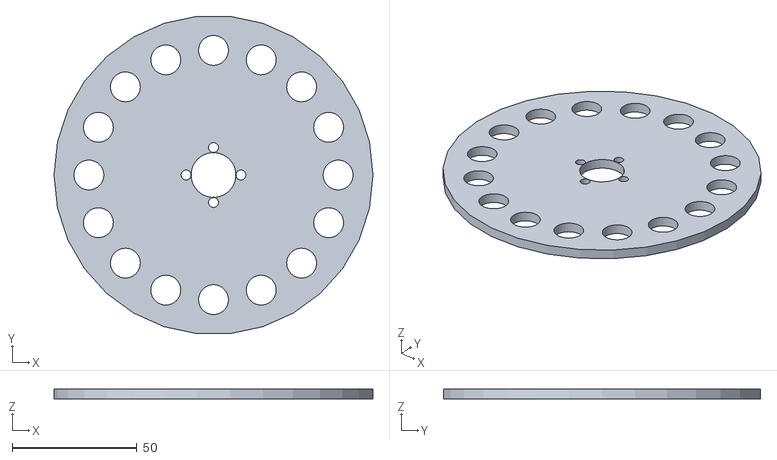
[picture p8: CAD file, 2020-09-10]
mechanical/shaker_3.stl
128.0 x 127.3 x 4.00

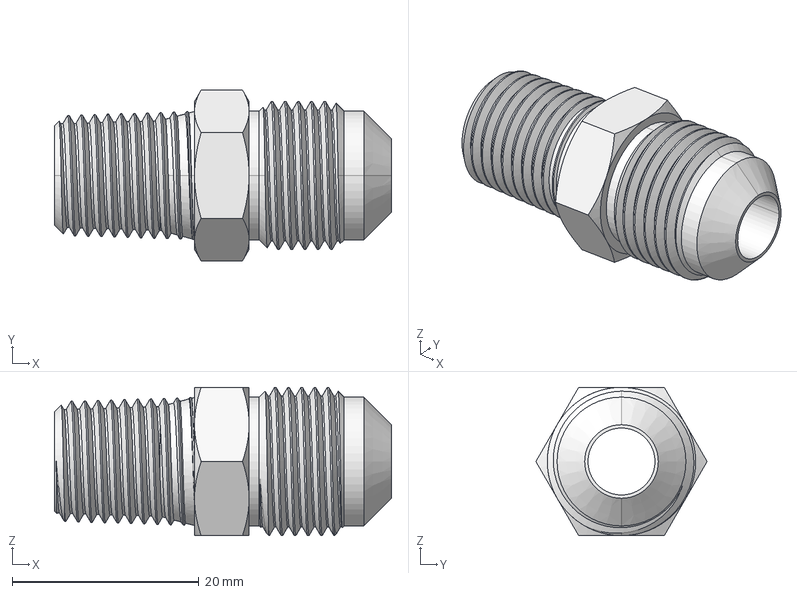
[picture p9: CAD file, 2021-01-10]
mechanical/vacuum_digitizer/frontplate.fcstd
36.1 x 18.3 x 15.9 mm

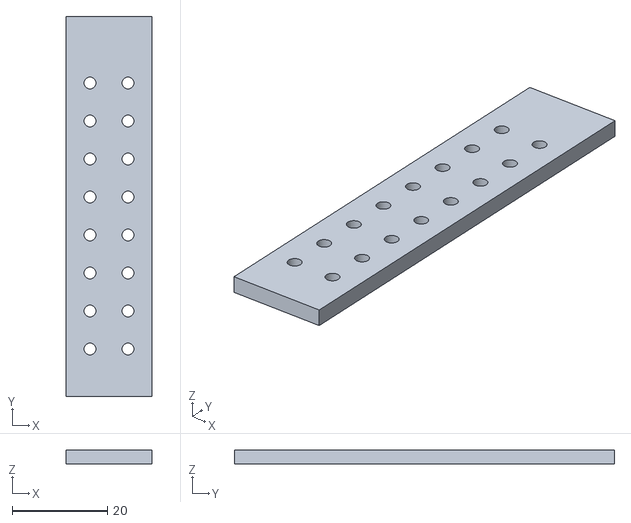
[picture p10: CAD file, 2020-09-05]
mechanical/microwell.stl
18.0 x 80.0 x 3.00

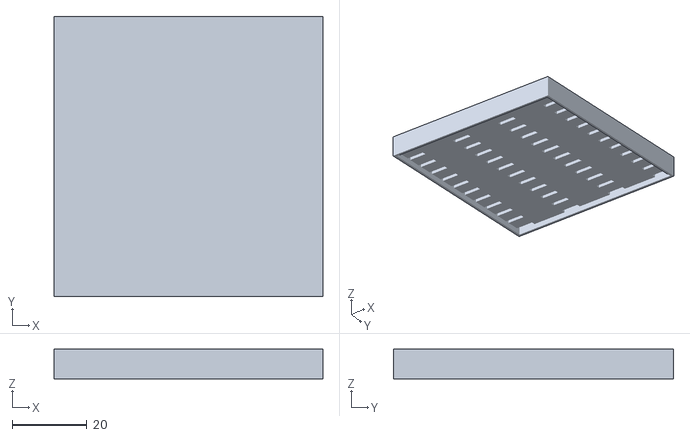
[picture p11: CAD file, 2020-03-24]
mechanical/mk1-5_furnace/insulator2.stl
72.0 x 75.0 x 8.00

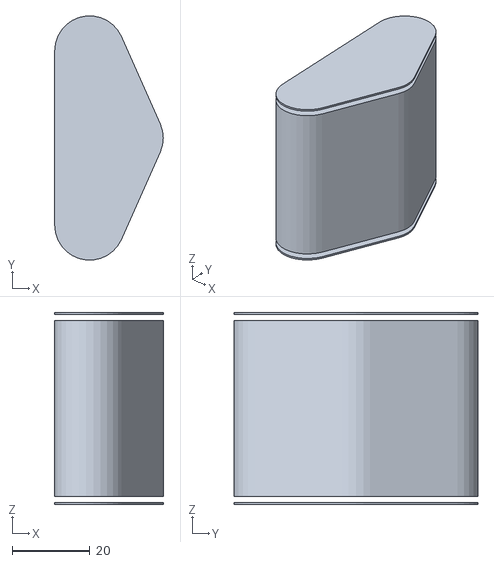
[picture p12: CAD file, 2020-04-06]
mechanical/Mk2-2_furnace/mechanical/test.stl
28.0 x 62.9 x 49.5

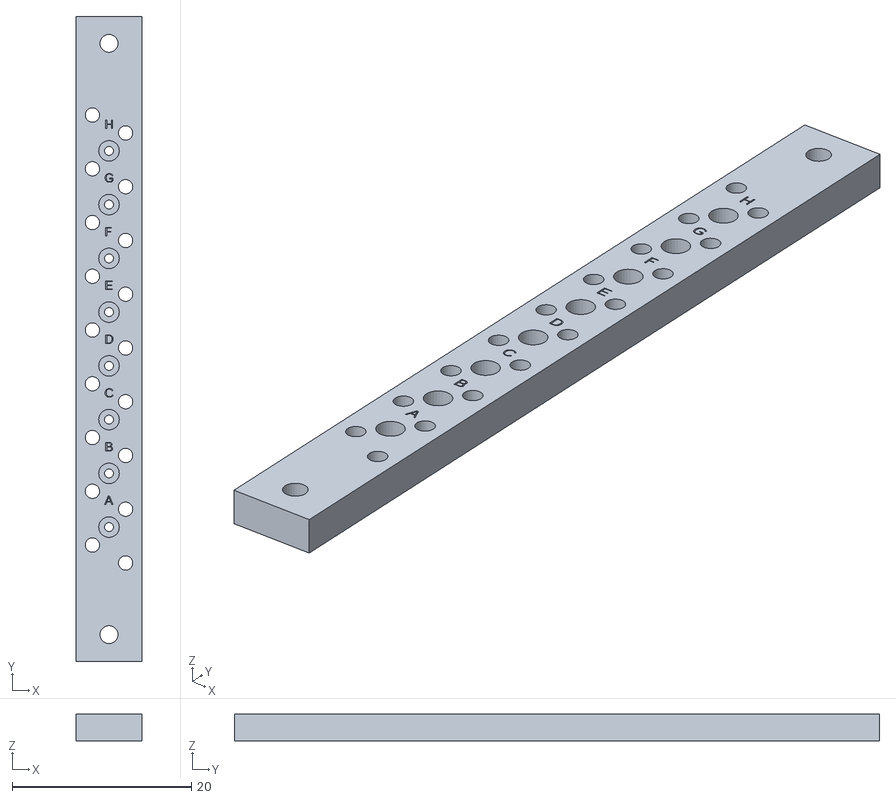
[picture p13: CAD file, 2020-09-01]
mechanical/dowel_plate_3.stl
7.41 x 72.0 x 3.00

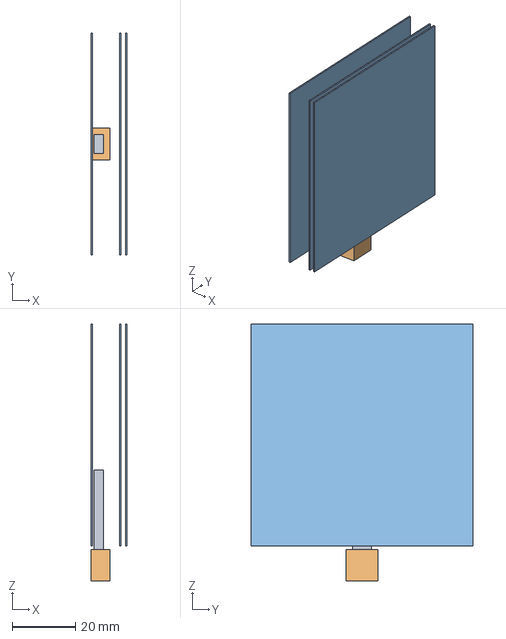
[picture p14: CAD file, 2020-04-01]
mechanical/Mk2-2_furnace/mechanical/test1.step
11.5 x 70.0 x 81.0 mm

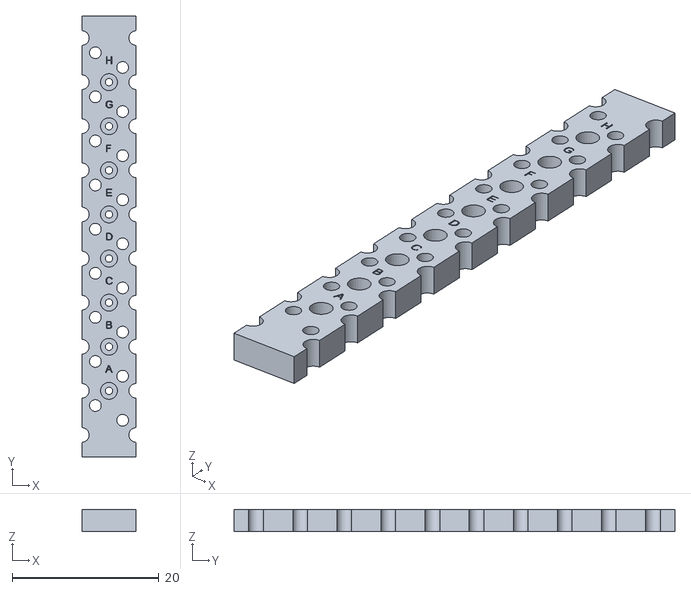
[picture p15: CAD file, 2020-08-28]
mechanical/dowel_plate_2.stl
7.41 x 60.0 x 3.00

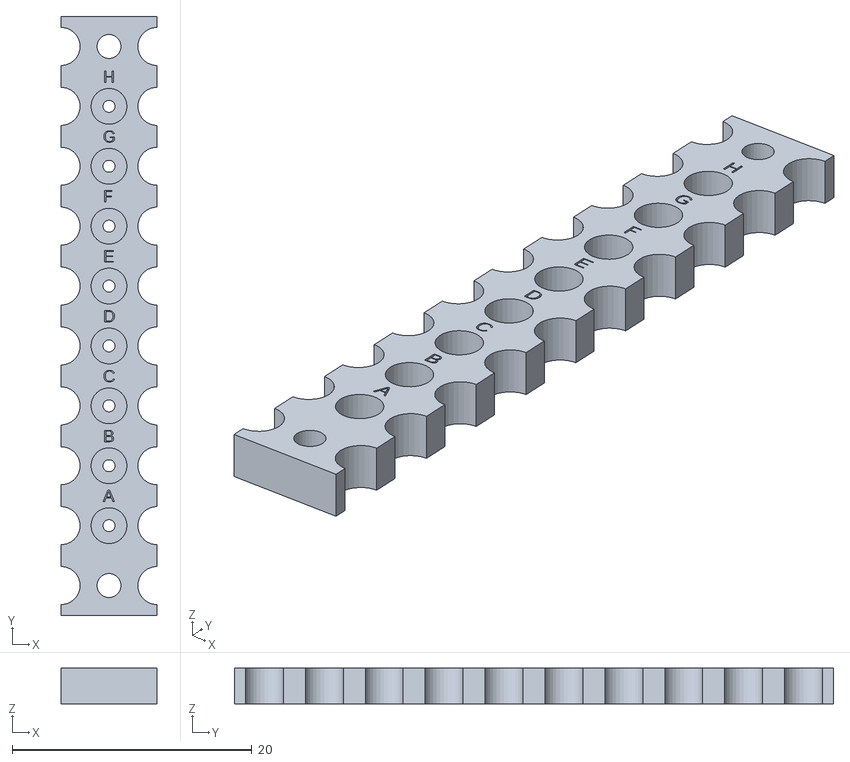
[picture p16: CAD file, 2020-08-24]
mechanical/plate.stl
8.00 x 50.0 x 3.00

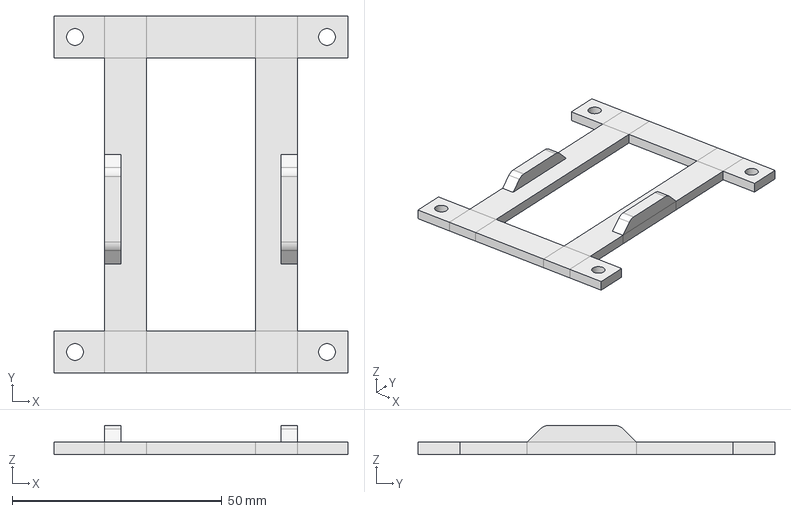
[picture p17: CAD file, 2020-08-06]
mechanical/preload_plate.FCStd
70.0 x 85.0 x 7.00 mm

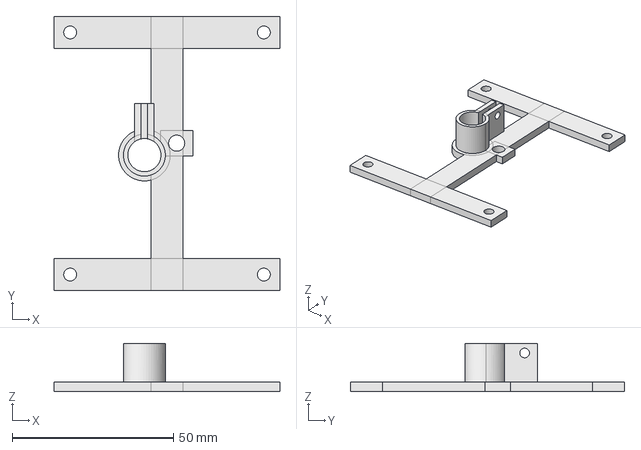
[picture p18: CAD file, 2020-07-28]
mechanical/sensor_arm.FCStd
70.0 x 85.0 x 15.0 mm

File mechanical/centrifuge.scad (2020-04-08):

$fn = 40;

eppendorf_hole_diameter = 11.5;

extra_radius = 2;

shaft_diameter = 5;

//translate([0,0,8]) cylinder(d=8,h=15);


difference(){
    cylinder(d=70,h=8);
    union(){
        for(i = [0:3]){
            rotate(a=[0,0,i*(360/4)]){
                rotate(a=[-35,0,0]){
                    translate([0,-22,-20]) cylinder(d=eppendorf_hole_diameter,h=20);
                }
            }
        }

        for(i = [0:3]){
            rotate(a=[0,0,i*(360/4)+45]){
                translate([0,-45,0]) cylinder(d=40,h=20);
            }
        }
        translate([0,0,0]) cylinder(d=shaft_diameter+0.5,h=15);
    }
}

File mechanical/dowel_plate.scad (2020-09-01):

num_cuvettes = 8;
$fn = 30;

//Edges should be broken with a ball-nose end mill.

cuvette_diameter = 1.0;
cuvette_bottom_margin = 0;
cuvette_depth = 0.7;

cuvette_spacing = 6.0;

access_hole_diameter = 2.3;

alignment_pin_diameter = 2;
alignment_pin_x_offset = 3.5-(0.17500/2);

dowel_pin_diameter = 1.6;

slide_length = (cuvette_spacing) * num_cuvettes + 4*cuvette_spacing;

slide_height = 3.0;
slide_width = 3 + alignment_pin_diameter/2 + alignment_pin_x_offset;

x_centerline = slide_width / 2.0;

hole_margin = 2.0;

echo(slide_length);
echo(slide_width);

text_height = 0.5;
text_size = 1;
alpha = "ABCDEFGHIJKLMNOP";

difference(){
    cube([slide_width, slide_length, slide_height], false);
    
    union(){
        for (i = [-2:num_cuvettes+1]){
            y_centerline = i*cuvette_spacing + 2.5*cuvette_spacing;
            
            if(!(i < 0 || i >= num_cuvettes)){
                translate([x_centerline, y_centerline, cuvette_bottom_margin])
                       cylinder(slide_height - (cuvette_bottom_margin+cuvette_depth)+1,
                                        d=cuvette_diameter,center=false);
                    
                translate([x_centerline, y_centerline, cuvette_bottom_margin+cuvette_depth])
                       cylinder(slide_height - (cuvette_bottom_margin+cuvette_depth)+1,
                                        d=access_hole_diameter,center=false);
                
                translate([x_centerline-text_size/2, y_centerline+cuvette_spacing/2-text_size/2, slide_height - text_height])             linear_extrude(text_height){ text(alpha[i], text_size); };
                
        
            }
                    
//            translate([0, y_centerline, cuvette_bottom_margin])
//                   cylinder(slide_height,
//                                    d=alignment_pin_diameter,center=false);
//            
//            translate([slide_width, y_centerline, cuvette_bottom_margin])
//                   cylinder(slide_height,
//                                    d=alignment_pin_diameter,center=false);
//            
            if(!(i < 0 || i == num_cuvettes+1)){
                translate([x_centerline*1.5, y_centerline-cuvette_spacing/1.5, cuvette_bottom_margin])
                       cylinder(slide_height,
                                        d=dowel_pin_diameter,center=false);
                translate([x_centerline*0.5, y_centerline-cuvette_spacing/3, cuvette_bottom_margin])
                       cylinder(slide_height,
                                        d=dowel_pin_diameter,center=false);
            }
            
         
        }
   
        
        translate([x_centerline, cuvette_spacing/2, 0])
            cylinder(h=slide_height+1, d=2.0);
        translate([x_centerline, slide_length-cuvette_spacing/2, 0])
            cylinder(h=slide_height+1, d=2.0);
            
       
    }
}



//         translate([x_centerline+access_hole_diameter/2+hole_margin, y_centerline-access_hole_diameter/2,0])/
//cube([10, access_hole_diameter, slide_height - (cuvette_bottom_margin+cuvette_depth)+1],center=false);

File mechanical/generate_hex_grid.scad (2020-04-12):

// Thanks to the extremely detailad information @ http://www.redblobgames.com/grids/hexagons/
// I was able to generate this circular hexagonal grid generator about a circle given an external
// perimeter radius, radius of each individual hexagon, and gap between each hexagon.
//
// Using the excerpts from the range section of the site
// http://www.redblobgames.com/grids/hexagons/#range 
// I was able to generate a list of cube coordinate points and convert them to cartesian 
// points for placing cylinders
//
//for each -N ≤ dx ≤ N:
//    for each -N ≤ dy ≤ N:
//        for each -N ≤ dz ≤ N:
//            if dx + dy + dz = 0:
//                results.append(cube_add(center, Cube(dx, dy, dz)))
//
// more efficient method: unsure if this method could be implemented or not, can't wrap my head
// around the conversion in OpenSCAD.
//
//for each -N ≤ dx ≤ N:
//    for each max(-N, -dx-N) ≤ dy ≤ min(N, -dx+N):
//        var dz = -dx-dy
//        results.append(cube_add(center, Cube(dx, dy, dz)))
//
//function hex_to_pixel(hex):
//    x = size * sqrt(3) * (hex.q + hex.r/2)
//    y = size * 3/2 * hex.r
//    return Point(x, y)
//
// Usage: generate_hex_grid(external_radius=100,radius=10,gap=.5,height=1)
// Parameters: 
//      external_radius: radius of bound circle to generate hex grid in
//      radius: radius of the fake heagons
//      gap: distance between hexagons


// example removing generated hex grid from cylinder
difference(){
    cylinder(r=100,h=2,center=true);
    generate_hex_grid(radius=14,height=3,gap=4);
}

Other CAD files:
mechanical/vacuum_digitizer/backplate.FCStd
mechanical/dowel_plate.stl
mechanical/drum.FCStd
mechanical/nephelometer.FCStd
mechanical/microwell.scad
mechanical/Mk2-2_furnace/mechanical/MLI.scad
mechanical/Mk2-2_furnace/mechanical/base.scad
mechanical/Mk2-2_furnace/mechanical/graphite_MLI.scad
mechanical/Mk2-2_furnace/mechanical/test_1.FCStd
mechanical/centrifuge.stl
mechanical/microfluidic/output.scad
mechanical/microfluidic/slide_id_1/frame.scad
mechanical/microfluidic/slide_id_1/layer_0.scad
mechanical/microfluidic/slide_id_1/layer_1.scad
mechanical/microfluidic/slide_id_1/layer_2.scad
mechanical/microfluidic/slide_id_1/layer_3.scad
mechanical/mk1-5_furnace/insulator.scad
mechanical/mk1-5_furnace/insulator2.scad
mechanical/mk1-5_furnace/roundedcube.scad
mechanical/plate.scad
mechanical/preload_plate.scad
mechanical/preload_plate.stl
mechanical/sensor_arm.stl
mechanical/shaker_2.scad
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

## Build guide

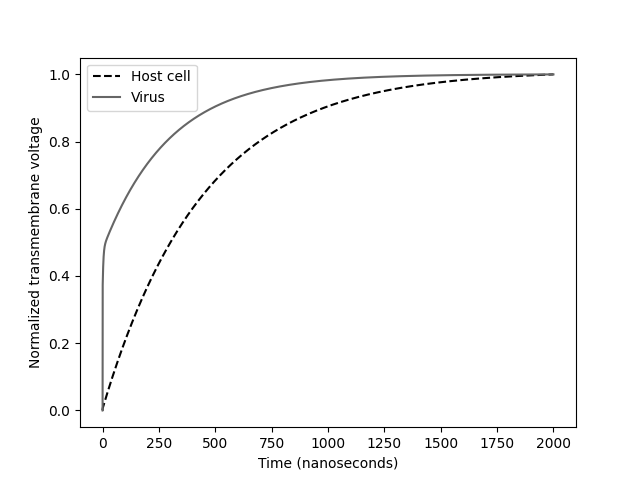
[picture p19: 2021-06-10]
biology/kotnik_transmembrane/plots/step_course.png

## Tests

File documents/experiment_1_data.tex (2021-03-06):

%!TeX root = experiment_1_data
\documentclass[paper.tex]{subfiles}
\begin{document}

\subsection{Data from testing on bacteriophage T4}

\begin{table}[h!]
	\centering
	\begin{tabular}{ |c|c|c|c| } 
				\hline
		\multicolumn{3}{|c|}{\textbf{Calibration trials} } \\
		\hline
		\hline
		Exposure & kilocounts per 10s integration & Note \# \\
		\hline
		Autoclaved phage (0.2 mL) & 30 & \\ 
		Autoclaved p. (50 uL) & 32 & Run 8\\ 
		\hline
		Phage culture 'blank' & 8 & \\ 
		Water & 1 & \\

		\hline
\multicolumn{3}{|c|}{\textbf{Pulsed CW trials}} \\
\hline

		\hline
		\multicolumn{3}{|c|}{\textbf{NF capillary}, 6 to 12 GHz, 10 or 20 us CW pulses, 85 V/m to 339 V/m expected} \\
		\hline
		Sham   & 12 & Run 8 t4,5...\\
		+ & 11 & Run 8 t4,5...\\
		+  & 12 & Run 8 t4,5...\\
		+  & 12 & Run 8 t4,5...\\
		\hline
		\multicolumn{3}{|c|}{\textbf{NF capillary}, 6 to 12 GHz, phage degraded with basic buffer, 85 V/m to 339 V/m expected} \\
		\hline
		Blank (0 min) & 14 & Run 9 \\
		Blank (\ntilde 15 min) & 17 & Run 9\\
		Sham (\ntilde 15 min) & 5 & Run 9\\
		Blank (\ntilde 4 hr) & 24 & Run 9\\
		\hline
		+  & 14 & Run 11\\
		Sham & 17 & Run 11\\
		\hline
		\multicolumn{3}{|c|}{\textbf{NF capillary}, 6 to 12 GHz, 10 or 20 us CW pulses} \\
		\hline
		Sham & 12 & Run 12\\
		+    & 10 & Run 12\\
		\hline
		\multicolumn{3}{|c|}{\textbf{0.2 mm channel}, 6 to 12 GHz, 10 or 20 us CW pulses, 200 V/m to 850 V/m exp., 10.6 kV/m pk} \\
		\hline
		 Sham & 12 & CPWG micro-\\
 		 +    & 10 & CPWG micro-\\

		\hline
		\multicolumn{3}{|c|}{\textbf{Nanosecond pulsed trials} } \\
		\hline

 		\hline
		\multicolumn{3}{|c|}{\ntilde 0.2 mm channel, various pulse counts and termination, 0.155 MV/m expected, 5.6 MV/m peak} \\
		\hline 
		 Blank    & 8 & Li test 1\\
		 +           & 8 & Li test 1\\
 		 +           & 7 & Li test 1\\
 		 +           & 7 & Li test 1\\
 		 + \& shaper & 7 & Li test 1\\
 		 \hline

		\multicolumn{3}{|c|}{\ntilde 0.03 mm channel, 0.2 uL/s, various pulse counts and termination, 1 MV/m expected, 38 MV/m peak} \\
		\hline
		Sham & 5 & Smaller \\
		+ & 6 & Smaller \\ 
		+ & 6 & Smaller  \\ 
		\hline

		\multicolumn{3}{|c|}{\ntilde 0.03 mm channel, basic buffer, tainted as pH may not have been 10.6, 1 MV/m exp., 38 MV/m pk} \\
		\hline
		Sham & 12 & Weakened \\  
		Blank & 11 & Weakened  \\ 
		Blank & 12 & Weakened  \\ 
		Blank & 9 & Weakened  \\ 
		+ & 11 & Weakened \\
		+ (no term) & 11 & Weakened \\ 
		+ & 9 & Weakened \\ 
		\hline
	\end{tabular}
\end{table}
%how many pulses?

Original notes for this table can be inspected at \ghfile{firmware/eppenwolf/pulse_1.pnw}. Data rounded to the nearest thousand fluorescence photon counts per 10 seconds. Larger numbers are presumed to correlate with greater capsid damage (see Autoclaved).

Note the width of the electric field bounds. These are not meaningful random or systematic intervals; we can only confidently assert that the field did not exceed the peak value at any point within the channel. Expected values based on FDTD simulation and voltage; peak based on channel width and voltage.

See notes on experiment design and data collection in main body and GitHub supplemental.

\end{document}

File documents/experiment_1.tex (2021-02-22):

%!TeX root = experiment_1
\documentclass[paper.tex]{subfiles}
\begin{document}

\section{Experiment 1: Attempts at microwave absorption spectroscopy and inactivation in the microsecond pulsed 100 V/m regime}

\subsection{Introduction}

Rationale for using T4

\begin{autem}
As noted, this field reached a reasonable level of quality. 1951. Some standards.
By using yet another design, with a new set of unknown artifacts, we are actually hampering this field;
and so we encourage anyone who may wish to replicate this result not to use this system, but one of the better-characterized systems mentioned below.
In this case, we are limited by budget - primarily the power amplifiers we have access to.
\end{autem}

Positions of the three quantities on the slide are randomized\cite{first2000}.

We have tried to comply with the guidelines

Our aims with this experiment were to perform the following:

\begin{itemize}
	\item Convince ourselves that our skepticsm is unjustified.
	\item Crudely demonstrate the pulse hypothesis.
	\item Simulataneously, avoid any ambiguity related to the 7 C temperature rise seen in the previous paper.
	\item Test the microwave lysis feedback
	\item Verify the damage feedback mechanism.
	\item Demonstrate a cheap microwave spectrometer that could be used on NCoV.
\end{itemize}

This was very dumb.

Demonstrate the effect in a pulsed manner.

A pulse appears to be more easily applicable in the clinic. \cite{Efficient2015}'s use of a 15 minute exposure caused us some consternation
- had we missed something; was it possible that inactivation could take so long?

second, it mitigates any possible thermal effect that could have lead to the previous results.

Our justification for wanting a pulse dataset is as follows:

A temperature rise of 7 deg C was found at 6 GHz.

[] found detectable mutagenicity at a mere 2 C temperature rise.
Of course, a few SNPs here and there is not complete cell lysis; it is extremely implausible that
the results were the result of the temperature rise. But we nonetheless wanted to control this factor if possible.

The antenna gain increases with frequency (naturally - it goes as aperture size / lambda).
The gain flatness of the amplifier used is specified at [].
If the exposure power was measured at the input to the amplifier (the method of power measurement does not appear to be mentioned), is it not
unreasonable to expect that perhaps, at 9 GHz, the temperature rise, at some point in the 15 minute test, reached 15 C?

This is all post-hoc reasoning. It strains plausibility. If we consider how many negative results went unpublished;
if we presume that 50 other teams found no effect, is it possible that this is a 1 in 50 fluke?

Because the diode detectors are in an extremely noisy environment, it was found useful to immediately digitize the signal within a mm of the output. Care in shielding may alleviate this issue.

In the end, performing this was probably a mistake and unecessary, but by the time we realized this we had already put in the bulk of the time.

Inspired by \cite{Biocoder2010}, we originally planned on writing the microbiology protocol directly into the {\it Eppenwolf} firmware using \cite{Noweb}.
However, because the device was planned to run headless in a BSL, this was abandoned.

The method we use is terrible. Such small volumes pose incredible headaches and low SNR for little reason.
Ideally, we should have used a technique orthogonal to previous studies.

We later found the following paper on phase fluctuation optical heterodyne spectroscopy \cite{Broadband1988}, which solves essentially all issues surrounding. Arguably no biological-resonance studies should ever be conducted on any less than such a setup.
it "[requires] that only perfunctory attention be paid to the sample geometry.", and "allows very straightforward determination of the free-space absorption
coefficient of the sample based on the photothermal signals measured as a function of distance along the transmission line."

"This spectroscopic technique stands in contrast to the time-domain reflectometer and network-analyzer techniques-not
zero-background methods-that require the measurement of small changes in large signals."

It uses a phase-sensing, providing a 1 microdegree temperature measurement.

This requires no special equipment beyond standard optical lab supplies - mirrors, servoing piezo stages.

Microwave dielectric spectrometry ("impedance spectroscopy", "absorption spectroscopy")

The notable Feldman biological spectroscopy group recommends a time-domain spectroscopy method\cite{Time2003a}, a modification of beloved TDR techniques. They cite several advantages, including easy subtraction of test jig artifacts.
Generating a sharp-edged impulse with 10+ GHz spectral components is far easier and cheaper than an equivalent CW oscillator; but then we could not simultaneously expose the virus to the pulsed CW tone to verify the inactivation field thresholds.
A 10+ GHz oscilloscope is generally required for this method, but sampling\footnotemark oscilloscopes may suffice. \cite{16psresolution2003} offer a simple way to do away with the delay lines that are usually required.

\footnotetext{Confusing name - a 'sampling oscilloscope' builds up the waveform over a large number of cycles.}

On the other hand, putting the sample into a microwave cavity resonator can often provide a much higher sensitivity. The sensitivity can (in some cases - there are tradeoffs - see \cite{FabryPerot1982}) be made proportional to the Q, and even a crude microwave cavity can easily have a Q > 500.
As an example, EPR spectrometers use cavities in their microwave bridges.

Cavities designed for wide-band use are generally mechanically tuned with a shorting plunger; the plunger itself presents difficulty in design\cite{Contactless2019}.
However, conventional waveguide cavities run into overlapping modes beyond half an octave, beyond which more than one dimension must usually be altered. We desired a spectrum across the entire 6 - 12 GHz octave.

Open-ended coaxial resonators can offer the required tuning range\cite{Wideband1981}\cite{Study2014a}. Microwave Fabry-Perot etalons are also satisfactory.\cite{FabryPerot1982}

The status quou for measuring the dielectric properties of liquid is an open-ended coax dipped in the solution\cite{Coaxial1980}. However, these appear to be particularly prone to generating resonance-like artifacts - not that the coplanar method is necessarily any better.

We end up using the coplanar waveguide setup, essentially exactly like \cite{Efficient2015}. Rather than expose the sample separately in a horn antenna, the entirety of the sample is held in the fringe field of the coplanar waveguide.
This was done because of our lack of access to power amplifiers with sufficient power output to expose a large volume simultaneously; however, it ends up an andvantage, because the spectra of the sample can be obtained immediately before and after exposure without disturbance.

Rather than the very professional gold and SiO2-coated sensing structure, we use a basic $50\pm20$ ohm coplanar waveguide, like \cite{Sun}.

An FDTD simulation was performed of the cuvette-waveguide assembly\footnotemark. The bottom tape was made 0.5 mm thick in the simulation dielectric\_constant, and non-conductive\footnotemark. Amplitude values were obtained with a soft 50 ohm source with a 1 V peak (2v p-p) (which would produce a value of 0.5 V minus the (Shottky drop and a small frequency-dependent loss) on the detectors).

The fringe field in the bottom 40\% (0.4 mm) of the fluid-filled well averaged 160 V/m per volt of uncorrected detector input amplitude, with a peak of 200 $\frac{V/m}{V}$ and two hot-spots at the interfaces of < 0.1 mm each. The remaining 60\% (0.6 mm) decreased from 120 $\frac{V/m}{V}$ to 60 $\frac{V/m}{V}$.

\footnotetext{TODO: Update sim to new cuvette dimensions}

\footnotetext{TODO: Update sim real phage fluid conductivity}

[cpwg sim here]

The sample is held against the waveguide in a cylindrical well 1 mm in diameter and approx. 1 mm high, in a 3 mm high machined polycarbonate slide, 8 wells per slide.\footnotemark This is aligned on the spectrometer with plastic dowel pins. 0.8 uL of sample are added to each well using a micropipette. A 0.06 mm silicone-adhesive Kapton tape insulates the fluid from the waveguide ()
Evaporation was very significant even if the top of the well was sealed with tape, so the cuvette is capped with a layer of silicone oil in a 2.3 mm opening; this worked very effectively.

[detail of slide]

\footnotetext{Off-the-shelf 1536-well plates have similar dimensions and could be substituted in the future.}

Such small volumes caused us no end of difficulty. It is very difficult to obtain a log-phase culture required; but, conversely, it is impossible to consistently add reagents or retrieve the sample after the silicone cap is added, so all the ingredients for the assay must be added before.

Needless to say, this is definitely not the correct way to go about this. However, it seems provide acceptable data for these purposes.

Conventional microstrip produces a considerably larger fringe field. However, the ground plane in microstrip is on the bottom layer. The sensitive QFN device ground pins would need to be stitched from the top to the bottom, inevitably adding all sorts of weird and wonderful resonators.
We were not able to prototype with vias with sufficiently low inductance to negate thise issues; so a single-layer, top-side-only stackup is used. The difference in performance and in ease of layout and routing is tremendous.

Coplanar waveguides are usually designed with a ground plane and via stitching on either side (GCPW), which both improves isolation and noise, but also helps to avoid parallel-plate propagation modes(\cite{Microwaves101c}, \cite{Propagation1990}, \cite{Characteristics1997}). Not including a ground plane avoids these modes, but decreases the available fringe field slightly. We did not add a ground plane.

The well is covered

We have tried to follow the study design best practices of \cite{Biological2016}:

\section{Blinding}

\section{Dosimetry}

Here we are slightly deficient. Other

\section{Positive control}

\cite{Efficient2015} use freeze-thaw cycles to crack the viral capsid as a positive control.
T4 appeared to be more resistant to freezing; therefore, our positive control is the aforementioned autoclaved phage.

Not having a sonication probe or Electroporator

\section{Sham controls}

Properties:

active phage/sterile broth/autoclaved phage/dilute phage in saliva
e. coli / no e. coli (sterile broth)
300 exposed / 200 exposed / 100 exposed / un- or sham-exposed
1 unit time pulse-exposed / 10 unit time pulse-exposed / continuous-exposed
on-resonance exposed / off-resonance exposed

Of these, the following combinations make sense:

"negative control": Active phage \& e. coli \& sham-exposed
"e.coli control": Sterile broth \& e. coli \& sham-exposed
"sterility control": Sterile broth \& no e. coli \& sham-exposed
"positive control": Autoclaved phage \& e. coli \& sham-exposed
"continuous trial": Autoclaved phage \& e. coli \& sham-exposed

Each on two plates.

The signal used was spectrally impure; phase noise was very high. However, all spurs are at about 3 dB down.

VCO voltages were calibrated to frequencies using a HackRF One and an HMC /8 frequency divider.

(A downconverter using an HMB and a custom 6.4 GHz LO was tried, but it was found that this was much less informative and more confusing
due to a lack of effective mixer image and LO spur rejection.)

It is possible to subtract the diode drop using [], but because of design flaws in the AC coupling of the detectors, this was not done.
A Shottky drop of 0.25 V is assumed in all cases.

- Un-exposed phage-only control:

Add 1 unit phage to cuvette. Monitor turbidity.

- Un-exposed e. coli control.
- Exposed e. coli control.
- Exposed phage control.
- Un-exposed e. coli + phage control
- Un-exposed e. coli + positive autoclaved phage control
- 1 - minute exposed

To preclude the possibility of damage to the sample while the spectrum is recorded.

0.3 V on a 50-ohm line is

%0.4 mW × 10 s / ((4 J / (g × K)) × 0.2 µL × (1 g / mL)) ➞ K

5 K

\subsection{Microwave lysis feedback}

We postulate the following. When the virus is lysed, the resonator is destroyed. This should be reflected in the impedance spectrum.
We would expect a non-reversible decrease in the resonance peak after the application of power. This should also appear in the time-domain pulse envelope; we expect a "notch" on the rising edge, with a slow taper upwards, which does not repeat on the next pulse.

If this exists, it would provide a great deal of feedback. Not only would the virus be destroyed, but we would have an instant, quantitative determination of of how effective each treatment was. In practice, this could be done by applying two pulses in quick succession and monitoring the change in the reflected power; or perhaps by a time-domain pulse-shape method. Whether such a signature can be discriminated from background in a clinical setting remains to be seen.

At the time, this seemed important to establish, as it would allow the inactivation threshold to be determined without a time-intensive and potentially dangerous infectivity assay step (making it more plausible that we would get biosafety approval to obtain the microwave spectrum of NCoV). 

One could imagine it to be otherwise. For instance, the lysis that occurs after phage infection of bacteria does little harm to the host cell; only the permeability of the membrane is damaged\cite{GROWTH}. Similarly, the results of the previous studies could perhaps have been obtained without necessarily destroying the virus' envelope.

\begin{center}
	\begin{tabular}{ |c|c|c|c| } 
		\hline
		col1 & col2 & col3 \\
		\hline
		\multirow{3}{4em}{Multiple row} 
		& cell2 & cell3 \\ 
		& cell5 & cell6 \\ 
		& cell8 & cell9 \\ 
		\hline
	\end{tabular}
\end{center}

All biasing and power supplies were programmable and sequenced via an arrangement of DACs and amplifiers.

The sample rate of the delta-sigma ADCs was not sufficient to capture the amplitude of the short pulses; therefore 

\begin{figure}[H]
	\centering

	.png}

\end{figure}

\begin{figure}[H]
	\centering
	
	.png}
	
\end{figure}

\subsection{Weakened phage capsid testing}

Ishii and Yanagida \cite{two1977} and Qin \cite{Structure2010} find at a pH of 10.6, about 0.3x inactivation after a few minutes of incubation at 37 C, slowly increasing to. The capsid is weakened greatly by the base, relying on the "clamp proteins" hoc and soc.

\section{Saturated salt solution}

100 g NaCl was added to 0.25 mL of PG1. 

counts only 5000.

pulse\_VCO(10000); and 0.20 deadly current. a consistent 2.96 V maximum was observed.

3200 counts on 0, exposed

ran a sham:

3200 counts.

darnit!

blank counts, with 1 ml water, are about 500.

\end{document}

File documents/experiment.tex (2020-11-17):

Rationale for using T4

Yang uses AFM data indicating a 0.14 MPa yield stress.

\cite{Osmotic2003} 30 atmospheres, and breaks at a pressure differential of 100 atm.
T4 stress

by $\sigma = pr / 2t $,
t = 7 nm, r = 60 nm, and p =

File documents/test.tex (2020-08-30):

\documentclass[fleqn,10pt]{paper}

\usepackage[left=2cm,right=2cm,
top=0.5cm,
bottom=1.5cm,%
headheight=11pt,%
letterpaper]{geometry}

\include{preamble}

\title{{\it Maxwell's Silver Hammer:}\\ On pulsed microwave acoustic resonant viral inactivation}

\begin{document}

\section{Silicon carbide test}

To verify that we can detect a resonance with this setup, we use the microwave susceptor mixture described by \cite{Effect2016}, which can be tuned to the correct range by varying the concentration of SiC to binder. We use the S-1 mixture.

0.6g 2000-mesh silicon carbide powder was added to 1.4 g white Elmer's glue, mixed manually until homogeneous,
applied to a mylar film, and dried with a hair dryer. A small wafer of the hardened mixture, perhaps 0.3 mm thick, 5 mm x 2 mm, was placed directly on top of the coplanar waveguide.

The spectrum was then captured, averaging (?10) sweeps of the VCO. The background spectrum was taken without the wafer in place.

\begin{figure}[H]
	\includesvg[width=\textwidth]{sic_9_1}
	\caption{}
\end{figure}

\begin{figure}[H]
	\includesvg[width=\textwidth]{sic_9_2}
	\caption{}
\end{figure}

\cite{Effect2016} measures a peak at about 7.2 GHz. Our peak is at approximately 7.849 GHz, which is well within variation in powder grain sizes and concentration.

The paper specifies the reflection loss, S$_{11}$. Unfortunately, having no directional couplers, it is probably not possible to directly determine S$_{21}$ and S$_{11}$ with this setup.

Naively, we might expect the peak to appear as a decrease at both sensors; instead it appears as an increase in transmission and decrease in reflection. It could be possible that the presence of the dielectric wafer has merely detuned an existing resonance, that the peak is a coincidence, and that these data mean nothing.
The raw voltage plots do not suggest that this is the case; but it is nonetheless concerning.

\footnote{The paper mentions that the "blending fraction of silicon carbide powders to epoxy resin was 30 \%, 35 \%, 40 \%, 45 \% and 50\% by weight". That seems a little ambiguous as to whether that's "weight per total mass" or "weight per epoxy".}

\end{document}

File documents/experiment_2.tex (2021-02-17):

%!TeX root = experiment_2
\documentclass[paper.tex]{subfiles}
\begin{document}

\section{Experiment 2: Attempts }

\subfile{pulse_generator}

\end{document}

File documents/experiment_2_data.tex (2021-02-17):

%!TeX root = experiment_2_data
\documentclass[paper.tex]{subfiles}
\begin{document}
	
\end{document}

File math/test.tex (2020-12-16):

\documentclass[]{article}

\usepackage{pdfpages}

\begin{document}

A qualitative statement of the problem, for context:

\begin{quote}
An arbitrary waveform, given in the frequency domain as $F(\omega)$, propagates through a dispersive, lossy medium. It then drives a damped harmonic oscillator that is initially at rest. \\

What $F$ produces the peak {\it transient} amplitude on the oscillator?

\end{quote}

(this might be completely ill-posed or otherwise intractable - I grasp very little of the below, unfortunately)

(there're lots of different approaches to this - Oughston's asympototic method, Macke and Segard - but this one seems sensible) \\

Zhu et al, in doi: 10.1109/APS.2012.6348428 offer a method to maximize the electric field $e_x(z,t)$, (see Franzen's fourier-transform method \\ http://www.dtic.mil/docs/citations/ADA371944)\\

Prof. Costas gave me a page (unpublished it seems) with more details - see the blue attached pdf.\\

Given

$$ e_x(z,t) = \frac{1}{\sqrt{2 \pi}} \int_{-\infty}^{+\infty}{F(\omega) e^{- j (\omega/c_0)n(\omega)z}\ e^{j\omega t} d\omega} $$

$$W = \frac{1}{\eta_0} \int_{-\infty}^{+\infty}{(n_r(\omega))\ |F(\omega)|^2}\ d\omega$$\\

Where $n(\omega)$ is a complex refractive index per Debye relaxation equation, $n_r()$ is the real part of the same, everything else is a real constant. Set up a functional with a lagrange multiplier\\

$$\xi = -e_x(z,t) + \lambda W$$\\

Take the functional ("variational") gradient with respect to $F(\omega)$.

$$ \nabla \xi = -\frac{1}{\sqrt{2\pi}} \left(e^{- j (\omega/c_0)n(\omega)z}\right)^\star \  e^{-j\omega T} + \lambda...$$

Where * is the complex conjugate.\\

The $\nabla H() = H()^\star$ thing seems to come from Franks, Signal Theory, 1969, page 140 onwards; I cannot make heads or tails of his formulation. \\

Neither Mathematica's VariationalD, Matlab's Fundiff, nor Maple's functionalDerivative seem to yield any meaningful result for grad xi.\\

Then set

$$\nabla \xi = 0$$

and solve for $F(\omega)$ normally. (then fourier transform back to $F(t)$, whatever)

\section{Harmonic oscillator Green's function}

From the below pdf, (renamed F(force) to $e_x$ to avoid confusion), where q is a charge, oscillation amplitude is

$$x(t) = \int_{-\infty}^{+\infty}{G(t,t')\ \frac{q\cdot e_x(z,t'))}{m}\ } dt'$$\\

Where G() is listed therein (eq. 15, for the underdamped case) (Keeping the Green function in the frequency-domain could maybe simplify things a bit? Wouldn't have to fourier-transform back and forth?)\\

Anyhow, then modify the lagrange multiplier,

$$\xi = -x(t) + \lambda W$$\\

And now,

$$\nabla \xi = 0$$

That seems to be the hard part.\\

How do you take the functional derivative of such an equation?

\includepdf[pages=-,pagecommand={}]{paper.pdf}

\includepdf[pages=-,pagecommand={}]{10_greens_function.pdf}

\end{document}

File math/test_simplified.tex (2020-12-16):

\documentclass[]{article}

\usepackage{pdfpages}

\begin{document}

Existing worked example from a paper:

$$ e_x(z,t) = \frac{1}{\sqrt{2 \pi}} \int_{-\infty}^{+\infty}{F(\omega) e^{- j (\omega/c_0)n(\omega)z}\ e^{j\omega t} d\omega} $$

$$W = \frac{1}{\eta_0} \int_{-\infty}^{+\infty}{(n_r(\omega))\ |F(\omega)|^2}\ d\omega$$\\

Where $n(\omega)$ is a complex function, $n_r()$ is the real part of the same, everything else is a real constant. An existing paper sets up the functional with a lagrange multiplier\\

$$\xi = -e_x(z,t) + \lambda W$$\\

Takes the functional ("variational") gradient with respect to $F(\omega)$.

$$ \nabla \xi = -\frac{1}{\sqrt{2\pi}} \left(e^{- j (\omega/c_0)n(\omega)z}\right)^\star \  e^{-j\omega T} + \lambda...$$

Where * is the complex conjugate.\\

The $\nabla H() = H()^\star$ thing seems to come from Franks, Signal Theory, 1969, page 140 onwards; I can't seem to make heads or tails of his formulation... \\

Neither Mathematica's VariationalD, Matlab's Fundiff, nor Maple's functionalDerivative seem to yield any meaningful result for grad xi, but I probably set things up wrong.\\

They then set

$$\nabla \xi = 0$$

and solve for $F(\omega)$ normally. (then fourier transform back to $F(t)$)\\

\pagebreak

What I'd like to do is modify this to maximize the amplitude x(t) of oscillation of a harmonic oscillator. Using the Greens function solution, \\

where q is a charge, oscillation amplitude is

listed therein (eq. 15, for the underdamped case).\\

Anyhow, then modify the lagrange multiplier,

$$\xi = -x(t) + \lambda W$$\\

And now,

$$\nabla \xi = 0$$

That seems to be the hard part.\\

Is there any chance you could suggest a route to attack this gradient?

\end{document}

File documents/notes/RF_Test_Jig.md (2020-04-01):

ToDo:

Measure 

Create 5.5GHz LO.

[https://en.wikipedia.org/wiki/FR-4#Properties](https://en.wikipedia.org/wiki/FR-4#Properties)

Dielectric constant: 4.35 @ 500 MHz, 4.34 @ 1 GHz

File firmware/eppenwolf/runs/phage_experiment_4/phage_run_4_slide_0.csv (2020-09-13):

RESET
0.0000000,0.0000000,5,5Make sure tee is running; and set tee file to the slide #
Remove cuvette, amplifier starting
0.00
0.00
0.00
0.00
0.00
0.00
0.00
0.00
0.00
0.00
0.00
0.00
0.00
0.00
0.00
0.00
0.00
0.00
0.00
0.00
0.00
0.00
0.00
0.00
0.00
0.00
0.00
0.00
0.00
0.00
0.00
0.00
0.00
0.00
0.00
0.00
0.00
0.00
0.00
0.00
0.00
0.00
0.00
0.00
0.00
0.00
0.00
0.00
0.00
0.00
0.00
0.00
0.00
0.00
0.00
0.00
0.00
0.00
0.00
0.00
0.00
0.00
0.00
0.00
0.00
0.00
0.00
0.00
0.00
0.00
0.00
0.00
0.00
0.00
0.00
0.00
0.00
0.00
0.00
0.00
0.00
0.00
0.00
0.00
0.00
0.00
0.00
0.00
0.00
0.00
0.00
0.00
0.00
0.00
0.00
0.00
0.00
0.00
0.00
0.00
0.00
0.00
0.00
0.00
0.00
0.00
0.00
0.00
0.00
0.00
0.00
0.00
0.00
0.00
0.00
0.00
0.00
0.00
0.00
0.00
0.00
0.00
0.00
0.00
0.00
0.00
0.00
0.00
0.00
0.00
0.00
0.00
0.00
0.00
0.00
0.00
0.00
0.00
0.00
0.00
0.00
Remove cuvette, amplifier starting
RESET
0.0000000,0.0000000,5,5
RESET
0.0000000,0.0000000,5,5Make sure tee is running; and set tee file to the slide #
Remove cuvette, amplifier starting
0.10
0.11
0.11
0.11
0.11
0.12
0.12
0.12
0.12
0.12
0.12
0.12
0.12
1.48
Remove cuvette, amplifier starting
0.09
0.11
0.11
0.11
0.11
0.12
0.12
0.12
0.12
0.12
0.12
0.12
0.12
0.12
0.12
0.12
0.12
0.13
0.13
0.13
0.13
0.13
0.13
0.13
0.13
0.13
0.13
0.13
0.14
0.14
0.14
0.14
0.14
0.14
0.14
0.14
0.14
0.14
0.14
0.14
0.15
0.15
0.15
0.15
0.15
0.15
0.15
0.15
0.15
0.15
0.16
0.16
0.16
0.16
0.16
0.16
0.16
0.16
0.16
0.16
0.17
0.17
0.17
0.17
0.17
0.17
0.17
0.17
0.18
0.18
0.18
0.18
0.18
0.18
0.18
0.18
0.19
0.19
0.19
0.19
0.19
0.19
0.19
0.20
0.20
0.20
0.20
0.74
========================================================
Please move to cuvette 0
========================================================
1
0.00,0.0028594,0.1481719,5,5,0.05,0.00,0.00,0.00,0.00,0.00,0,0,3.00,35559,1
0.05,0.0029375,0.1533125,5,5,0.05,0.00,0.00,0.00,0.00,0.00,0,0,3.00,35575,1
0.10,0.0031172,0.1605469,5,5,0.05,0.00,0.00,0.00,0.00,0.00,0,0,3.00,35590,1
0.15,0.0033359,0.1670469,5,5,0.05,0.00,0.00,0.00,0.00,0.00,0,0,3.00,35606,1
0.20,0.0036094,0.1758672,5,5,0.05,0.00,0.00,0.00,0.00,0.00,0,0,3.00,35621,1
0.25,0.0039453,0.1857344,5,5,0.05,0.00,0.00,0.00,0.00,0.00,0,0,3.00,35637,1
0.30,0.0043125,0.1950156,5,5,0.05,0.00,0.00,0.00,0.00,0.00,0,0,3.00,35652,1
0.35,0.0048125,0.2065625,5,5,0.05,0.00,0.00,0.00,0.00,0.00,0,0,3.00,35668,1
0.40,0.0054219,0.2194219,5,5,0.05,0.00,0.00,0.00,0.00,0.00,0,0,3.00,35683,1
0.45,0.0060156,0.2307578,5,5,0.05,0.00,0.00,0.00,0.00,0.00,0,0,3.00,35699,1
0.50,0.0067891,0.2453906,5,5,0.05,0.00,0.00,0.00,0.00,0.00,0,0,3.00,35714,1
0.55,0.0077734,0.2612969,5,4,0.05,0.00,0.00,0.00,0.00,0.00,0,0,3.00,35733,1
0.60,0.0087109,0.2756094,5,4,0.05,0.00,0.00,0.00,0.00,0.00,0,0,3.00,35749,1
0.65,0.0098203,0.2935781,5,4,0.05,0.00,0.00,0.00,0.00,0.00,0,0,3.00,35765,1
0.70,0.0109453,0.3092344,5,4,0.05,0.00,0.00,0.00,0.00,0.00,0,0,3.00,35780,1
0.75,0.0122422,0.3300000,5,4,0.05,0.00,0.00,0.00,0.00,0.00,0,0,3.00,35796,1
0.80,0.0136484,0.3525313,5,4,0.05,0.00,0.00,0.00,0.00,0.00,0,0,3.00,35811,1
0.85,0.0149453,0.3726563,5,4,0.05,0.00,0.00,0.00,0.00,0.00,0,0,3.00,35827,1
0.90,0.0163984,0.3987188,5,4,0.05,0.00,0.00,0.00,0.00,0.00,0,0,3.00,35842,1
0.95,0.0179688,0.4264531,5,4,0.05,0.00,0.00,0.00,0.00,0.00,0,0,3.00,35858,1
1.00,0.0193125,0.4502969,5,4,0.05,0.00,0.00,0.00,0.00,0.00,0,0,3.00,35873,1
1.05,0.0207969,0.4793907,5,4,0.05,0.00,0.00,0.00,0.00,0.00,0,0,3.00,35889,1
1.10,0.0224766,0.5082031,5,4,0.05,0.00,0.00,0.00,0.00,0.00,0,0,3.00,35904,1
1.15,0.0241641,0.5315313,5,3,0.05,0.00,0.00,0.00,0.00,0.00,0,0,3.00,35923,1
1.20,0.0261797,0.5599375,5,3,0.05,0.00,0.00,0.00,0.00,0.00,0,0,3.00,35939,1
1.25,0.0286953,0.5867813,5,3,0.05,0.00,0.00,0.00,0.00,0.00,0,0,3.00,35954,1
1.30,0.0311172,0.6069688,5,3,0.05,0.00,0.00,0.00,0.00,0.00,0,0,3.00,35970,1
1.35,0.0340703,0.6312500,5,3,0.05,0.00,0.00,0.00,0.00,0.00,0,0,3.00,35985,1
1.40,0.0368047,0.6509063,5,3,0.05,0.00,0.00,0.00,0.00,0.00,0,0,3.00,36001,1
1.45,0.0400625,0.6717500,5,3,0.05,0.00,0.00,0.00,0.00,0.00,0,0,3.00,36017,1
1.50,0.0434063,0.6904376,5,3,0.05,0.00,0.00,0.00,0.00,0.00,0,0,3.00,36032,1
1.55,0.0464609,0.7045938,5,3,0.05,28.69,27.85,27.61,27.24,26.61,0,0,3.00,36193,1
1.60,0.0516719,0.7306876,5,3,0.05,28.69,27.85,27.61,27.24,26.61,0,0,3.00,36209,1
1.65,0.0545547,0.7389688,5,3,0.05,28.69,27.85,27.61,27.24,26.61,0,0,3.00,36225,1
1.70,0.0575859,0.7451251,5,3,0.05,28.69,27.85,27.61,27.24,26.61,0,0,3.00,36241,1
1.75,0.0613906,0.7506875,5,3,0.05,28.69,27.85,27.61,27.24,26.61,0,0,3.00,36257,1
1.80,0.0653438,0.7561876,5,3,0.05,28.69,27.85,27.61,27.24,26.61,0,0,3.00,36273,1
1.85,0.0690469,0.7590938,5,3,0.05,28.69,27.85,27.61,27.24,26.61,0,0,3.00,36289,1
1.90,0.0733203,0.7631563,5,3,0.05,28.69,27.85,27.61,27.24,26.61,0,0,3.00,36305,1
1.95,0.0769688,0.7668750,5,3,0.05,28.69,27.85,27.61,27.24,26.61,0,0,3.00,36321,1
2.00,0.0812266,0.7699063,5,3,0.05,28.69,27.85,27.61,27.24,26.61,0,0,3.00,36337,1
2.05,0.0856016,0.7745000,5,3,0.05,28.69,27.85,27.61,27.24,26.61,0,0,3.00,36353,1
2.10,0.0894219,0.7779063,5,3,0.05,28.69,27.85,27.61,27.24,26.61,0,0,3.00,36369,1
2.15,0.0940000,0.7820313,5,3,0.05,28.69,27.85,27.61,27.24,26.61,0,0,3.00,36385,1
2.20,0.0989531,0.7862813,5,3,0.05,28.69,27.85,27.61,27.24,26.61,0,0,3.00,36401,1
2.25,0.1035547,0.7884688,5,3,0.05,28.69,27.85,27.61,27.24,26.61,0,0,3.00,36417,1
2.30,0.1089141,0.7913125,5,3,0.05,28.69,27.85,27.61,27.24,26.61,0,0,3.00,36433,1
2.35,0.1155078,0.7950000,5,3,0.05,28.69,27.85,27.61,27.24,26.61,0,0,3.00,36449,1
2.40,0.1211719,0.7963125,5,3,0.05,28.69,27.85,27.61,27.24,26.61,0,0,3.00,36465,1
2.45,0.1268828,0.7974688,5,3,0.05,28.69,27.85,27.61,27.24,26.61,0,0,3.00,36481,1
2.50,0.1336484,0.7991563,5,3,0.05,28.69,27.85,27.61,27.24,26.61,0,0,3.00,36497,1
2.55,0.1393672,0.7989688,5,3,0.05,28.69,27.85,27.61,27.24,26.61,0,0,3.00,36513,1
2.60,0.1447969,0.7988438,5,3,0.05,28.69,27.85,27.61,27.24,26.61,0,0,3.00,36528,1
2.65,0.1497969,0.7951251,5,3,0.05,28.69,27.85,27.61,27.24,26.61,0,0,3.00,36544,1
2.70,0.1552578,0.7910313,5,3,0.05,28.69,27.85,27.61,27.24,26.61,0,0,3.00,36560,1
2.75,0.1600000,0.7815938,5,3,0.05,28.69,27.85,27.61,27.24,26.61,0,0,3.00,36576,1
2.80,0.1636484,0.7720625,5,3,0.05,28.69,27.85,27.61,27.24,26.61,0,0,3.00,36592,1
2.85,0.1665625,0.7597188,5,3,0.05,28.69,27.85,27.61,27.24,26.61,0,0,3.00,36608,1
2.90,0.1685391,0.7445938,5,3,0.05,28.69,27.85,27.61,27.24,26.61,0,0,3.00,36624,1
2.95,0.1700547,0.7305313,5,3,0.05,28.69,27.85,27.61,27.24,26.61,0,0,3.00,36640,1
3.00,0.1710234,0.7124375,5,3,0.05,28.69,27.85,27.61,27.24,26.61,0,0,3.00,36656,1
3.05,0.1708906,0.6926875,5,3,0.05,28.69,27.85,27.61,27.24,26.61,0,0,3.00,36672,1
3.10,0.1702109,0.6745625,5,3,0.05,28.69,27.85,27.61,27.24,26.61,0,0,3.00,36688,1
3.15,0.1692735,0.6501250,5,3,0.05,28.46,27.69,27.44,26.86,26.20,0,0,3.00,36850,1
3.20,0.1719609,0.6375625,5,3,0.05,28.46,27.69,27.44,26.86,26.20,0,0,3.00,36866,1
3.25,0.1689219,0.6086875,5,3,0.05,28.46,27.69,27.44,26.86,26.20,0,0,3.00,36882,1
3.30,0.1672813,0.5830938,5,3,0.05,28.46,27.69,27.44,26.86,26.20,0,0,3.00,36898,1
3.35,0.1663906,0.5624688,5,3,0.05,28.46,27.69,27.44,26.86,26.20,0,0,3.00,36914,1
3.40,0.1650078,0.5398438,5,3,0.05,28.46,27.69,27.44,26.86,26.20,0,0,3.00,36930,1
3.45,0.1631875,0.5183125,5,3,0.05,28.46,27.69,27.44,26.86,26.20,0,0,3.00,36946,1
3.50,0.1616719,0.5017501,5,3,0.05,28.46,27.69,27.44,26.86,26.20,0,0,3.00,36961,1
3.55,0.1596797,0.4839375,5,3,0.05,28.46,27.69,27.44,26.86,26.20,0,0,3.00,36977,1
3.60,0.1572969,0.4669375,5,3,0.05,28.46,27.69,27.44,26.86,26.20,0,0,3.00,36993,1
3.65,0.1553203,0.4533750,5,3,0.05,28.46,27.69,27.44,26.86,26.20,0,0,3.00,37009,1
3.70,0.1529844,0.4370000,5,3,0.05,28.46,27.69,27.44,26.86,26.20,0,0,3.00,37025,1
3.75,0.1511953,0.4215000,5,3,0.05,28.46,27.69,27.44,26.86,26.20,0,0,3.00,37041,1
3.80,0.1497891,0.4099688,5,3,0.05,28.46,27.69,27.44,26.86,26.20,0,0,3.00,37057,1
3.85,0.1487188,0.3962031,5,4,0.05,28.46,27.69,27.44,26.86,26.20,0,0,3.00,37077,1
3.90,0.1477813,0.3872032,5,4,0.05,28.46,27.69,27.44,26.86,26.20,0,0,3.00,37093,1
3.95,0.1470313,0.3769688,5,4,0.05,28.46,27.69,27.44,26.86,26.20,0,0,3.00,37109,1
4.00,0.1465859,0.3680938,5,4,0.05,28.46,27.69,27.44,26.86,26.20,0,0,3.00,37125,1
4.05,0.1466250,0.3619688,5,4,0.05,28.46,27.69,27.44,26.86,26.20,0,0,3.00,37141,1
4.10,0.1469766,0.3551875,5,4,0.05,28.46,27.69,27.44,26.86,26.20,0,0,3.00,37157,1
4.15,0.1477031,0.3501406,5,4,0.05,28.46,27.69,27.44,26.86,26.20,0,0,3.00,37173,1
4.20,0.1487500,0.3472813,5,4,0.05,28.46,27.69,27.44,26.86,26.20,0,0,3.00,37189,1
4.25,0.1503281,0.3458906,5,4,0.05,28.46,27.69,27.44,26.86,26.20,0,0,3.00,37205,1
4.30,0.1523359,0.3459844,5,4,0.05,28.46,27.69,27.44,26.86,26.20,0,0,3.00,37220,1
4.35,0.1544453,0.3470156,5,4,0.05,28.46,27.69,27.44,26.86,26.20,0,0,3.00,37236,1
4.40,0.1574922,0.3496719,5,4,0.05,28.46,27.69,27.44,26.86,26.20,0,0,3.00,37252,1
4.45,0.1609531,0.3538438,5,4,0.05,28.46,27.69,27.44,26.86,26.20,0,0,3.00,37268,1
4.50,0.1644219,0.3577813,5,4,0.05,28.46,27.69,27.44,26.86,26.20,0,0,3.00,37284,1
4.55,0.1686016,0.3640156,5,4,0.05,28.46,27.69,27.44,26.86,26.20,0,0,3.00,37300,1
4.60,0.1723984,0.3689531,5,4,0.05,28.46,27.69,27.44,26.86,26.20,0,0,3.00,37316,1
4.65,0.1770547,0.3762500,5,4,0.05,28.46,27.69,27.44,26.86,26.20,0,0,3.00,37332,1
4.70,0.1820859,0.3835938,5,4,0.05,28.46,27.69,27.44,26.86,26.20,0,0,3.00,37348,1
4.75,0.1866094,0.3903906,5,4,0.05,28.21,27.58,27.49,27.06,26.78,0,0,3.00,37510,1
4.80,0.1944063,0.4032500,5,4,0.05,28.21,27.58,27.49,27.06,26.78,0,0,3.00,37526,1
4.85,0.1980625,0.4101094,5,4,0.05,28.21,27.58,27.49,27.06,26.78,0,0,3.00,37542,1
4.90,0.2016016,0.4166719,5,4,0.05,28.21,27.58,27.49,27.06,26.78,0,0,3.00,37558,1
4.95,0.2055625,0.4246250,5,4,0.05,28.21,27.58,27.49,27.06,26.78,0,0,3.00,37574,1
5.00,0.2090156,0.4319844,5,4,0.05,28.21,27.58,27.49,27.06,26.78,0,0,3.00,37590,1
5.05,0.2113359,0.4373125,5,4,0.05,28.21,27.58,27.49,27.06,26.78,0,0,3.00,37606,1
5.10,0.2134297,0.4426094,5,4,0.05,28.21,27.58,27.49,27.06,26.78,0,0,3.00,37622,1
5.15,0.2143672,0.4456250,5,4,0.05,28.21,27.58,27.49,27.06,26.78,0,0,3.00,37638,1
5.20,0.2145625,0.4479688,5,4,0.05,28.21,27.58,27.49,27.06,26.78,0,0,3.00,37653,1
5.25,0.2136563,0.4488750,5,4,0.05,28.21,27.58,27.49,27.06,26.78,0,0,3.00,37669,1
5.30,0.2120469,0.4481094,5,4,0.05,28.21,27.58,27.49,27.06,26.78,0,0,3.00,37685,1
5.35,0.2095781,0.4461094,5,4,0.05,28.21,27.58,27.49,27.06,26.78,0,0,3.00,37701,1
5.40,0.2059219,0.4424219,5,4,0.05,28.21,27.58,27.49,27.06,26.78,0,0,3.00,37717,1
5.45,0.2022188,0.4384531,5,4,0.05,28.21,27.58,27.49,27.06,26.78,0,0,3.00,37733,1
5.50,0.1971563,0.4320000,5,4,0.05,28.21,27.58,27.49,27.06,26.78,0,0,3.00,37749,1
5.55,0.1912813,0.4246250,5,4,0.05,28.21,27.58,27.49,27.06,26.78,0,0,3.00,37765,1
5.60,0.1855781,0.4177032,5,4,0.05,28.21,27.58,27.49,27.06,26.78,0,0,3.00,37781,1
5.65,0.1792813,0.4087344,5,4,0.05,28.21,27.58,27.49,27.06,26.78,0,0,3.00,37797,1
5.70,0.1725078,0.3993594,5,4,0.05,28.21,27.58,27.49,27.06,26.78,0,0,3.00,37813,1
5.75,0.1665313,0.3913438,5,4,0.05,28.21,27.58,27.49,27.06,26.78,0,0,3.00,37829,1
5.80,0.1602500,0.3817031,5,4,0.05,28.21,27.58,27.49,27.06,26.78,0,0,3.00,37845,1
5.85,0.1544141,0.3736563,5,4,0.05,28.21,27.58,27.49,27.06,26.78,0,0,3.00,37861,1
5.90,0.1481406,0.3641250,5,4,0.05,28.21,27.58,27.49,27.06,26.78,0,0,3.00,37877,1
5.95,0.1420078,0.3549063,5,4,0.05,28.21,27.58,27.49,27.06,26.78,0,0,3.00,37893,1
6.00,0.1370547,0.3479063,5,4,0.05,28.21,27.58,27.49,27.06,26.78,0,0,3.00,37909,1
6.05,0.1315625,0.3394375,5,4,0.05,28.21,27.58,27.49,27.06,26.78,0,0,3.00,37925,1
6.10,0.1265859,0.3325469,5,4,0.05,28.21,27.58,27.49,27.06,26.78,0,0,3.00,37941,1
6.15,0.1227734,0.3272032,5,4,0.05,28.21,27.58,27.49,27.06,26.78,0,0,3.00,37957,1
6.20,0.1187813,0.3217969,5,4,0.05,28.21,27.58,27.49,27.06,26.78,0,0,3.00,37973,1
6.25,0.1147891,0.3169532,5,4,0.05,28.21,27.58,27.49,27.06,26.78,0,0,3.00,37989,1
6.30,0.1118359,0.3136563,5,4,0.05,28.21,27.58,27.49,27.06,26.78,0,0,3.00,38005,1
6.35,0.1087891,0.3103281,5,4,0.05,28.18,27.87,27.20,27.19,27.13,0,0,3.00,38166,1
6.40,0.1076250,0.3111719,5,4,0.05,28.18,27.87,27.20,27.19,27.13,0,0,3.00,38182,1
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

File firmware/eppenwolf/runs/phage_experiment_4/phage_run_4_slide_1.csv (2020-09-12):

RESET
Make sure tee is running; and set tee file to the slide #
Remove cuvette, amplifier starting
0.10
0.11
0.11
0.11
0.11
0.11
0.11
0.11
0.11
0.12
0.12
0.12
0.12
0.12
1.47
Remove cuvette, amplifier starting
0.09
0.11
0.11
0.11
0.11
0.11
0.11
0.11
0.11
0.11
0.12
0.12
0.12
0.12
0.12
0.12
0.12
0.12
0.12
0.12
0.13
0.13
0.13
0.13
0.13
0.13
0.13
0.13
0.13
0.13
0.14
0.14
0.14
0.14
0.14
0.14
0.14
0.14
0.14
0.14
0.14
0.15
0.15
0.15
0.15
0.15
0.15
0.15
0.15
0.15
0.15
0.15
0.16
0.16
0.16
0.16
0.16
0.16
0.16
0.16
0.16
0.17
0.17
0.17
0.17
0.17
0.17
0.17
0.17
0.17
0.18
0.18
0.18
0.18
0.18
0.18
0.18
0.19
0.19
0.19
0.19
0.19
0.19
0.20
0.20
0.20
0.20
0.74
========================================================
Please move to cuvette 0
========================================================
0
0.00,0.0026406,0.1499610,5,5,0.05,0.00,0.00,0.00,0.00,0.00,0,0,3.00,91623,0
0.05,0.0027188,0.1552031,5,5,0.05,0.00,0.00,0.00,0.00,0.00,0,0,3.00,91639,0
0.10,0.0029141,0.1623281,5,5,0.05,0.00,0.00,0.00,0.00,0.00,0,0,3.00,91654,0
0.15,0.0031094,0.1690234,5,5,0.05,0.00,0.00,0.00,0.00,0.00,0,0,3.00,91670,0
0.20,0.0033750,0.1778672,5,5,0.05,0.00,0.00,0.00,0.00,0.00,0,0,3.00,91685,0
0.25,0.0036875,0.1877578,5,5,0.05,0.00,0.00,0.00,0.00,0.00,0,0,3.00,91701,0
0.30,0.0040469,0.1969063,5,5,0.05,0.00,0.00,0.00,0.00,0.00,0,0,3.00,91716,0
0.35,0.0045078,0.2083047,5,5,0.05,0.00,0.00,0.00,0.00,0.00,0,0,3.00,91732,0
0.40,0.0051172,0.2213672,5,5,0.05,0.00,0.00,0.00,0.00,0.00,0,0,3.00,91747,0
0.45,0.0056953,0.2328672,5,5,0.05,0.00,0.00,0.00,0.00,0.00,0,0,3.00,91763,0
0.50,0.0064688,0.2476250,5,5,0.05,0.00,0.00,0.00,0.00,0.00,0,0,3.00,91778,0
0.55,0.0074453,0.2632813,5,4,0.05,0.00,0.00,0.00,0.00,0.00,0,0,3.00,91797,0
0.60,0.0083516,0.2771563,5,4,0.05,0.00,0.00,0.00,0.00,0.00,0,0,3.00,91813,0
0.65,0.0094609,0.2948906,5,4,0.05,0.00,0.00,0.00,0.00,0.00,0,0,3.00,91828,0
0.70,0.0106016,0.3103907,5,4,0.05,0.00,0.00,0.00,0.00,0.00,0,0,3.00,91844,0
0.75,0.0119297,0.3305625,5,4,0.05,0.00,0.00,0.00,0.00,0.00,0,0,3.00,91859,0
0.80,0.0133438,0.3523125,5,4,0.05,0.00,0.00,0.00,0.00,0.00,0,0,3.00,91875,0
0.85,0.0146641,0.3726250,5,4,0.05,0.00,0.00,0.00,0.00,0.00,0,0,3.00,91890,0
0.90,0.0161484,0.3988125,5,4,0.05,0.00,0.00,0.00,0.00,0.00,0,0,3.00,91906,0
0.95,0.0177266,0.4270000,5,4,0.05,0.00,0.00,0.00,0.00,0.00,0,0,3.00,91922,0
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

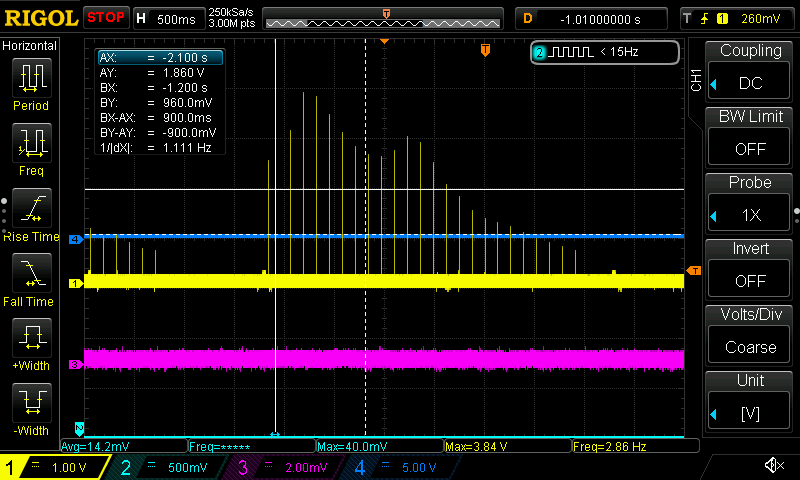
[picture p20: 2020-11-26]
firmware/eppenwolf/runs/phage_experiment_12/screenshot_192.168.0.38_2020-11-26_13:38:24.png

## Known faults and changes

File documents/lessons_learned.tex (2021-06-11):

%!TeX root = lessons_learned
\documentclass[paper.tex]{subfiles}
\begin{document}

\section{Lessons Learned} \

it seems like older papers that establish the base facts of a field, perhaps because of un-searchable full text, or a lack of recent citations directly,means there is some sort of bias towards more recent, but more detail-sparse papers.

PLoS One doesn't allow footnotes. This seemed weird, but trying to rewrite inline actually does seem to make things a lot cleaner, and I'll try to keep this.

I've been muttering a lot about saving the results of the simulations. However, perhaps the real solution is to never undergo this trial-and-error technique - to learn enough about the problem, and to have enough testing in place. This might not ever be feasible.

\rule{\linewidth}{0.2pt}

I've just realized something.

Experience. When I run a simulation and it errors out, the root cause of that error is *experience*. The plot that I generated and glanced over to inform the next set of parameters is *experience*. The way you pipette 0.5 uL of fluid is experience. 

maybe we need to digitize the experience of science. 

talk about the electroporation book saying that more effort in standardization is needed

%I hope that software should be written in a manner that is easy to support. This means documentation; reproducible builds; 

Not a fan of fortran, but it's actually remarkable in its longevity. A fortran code listing from the 1970s actually has a fair chance of running; has no dependencies, fully self-contained, etc.

Made a bonehead mistake while installing lanl-ansi fork of Ipopt. While screwing around in the very beginning, I had accidentally added to -L to the LDFLAGS environment variable. This completely broke the installation. I spent almost 4 hours trying to figure that out. I suppose having a list of commands would perhaps improve things...

LLIS

write in the highest-level language first , then translate. 

the os community has figured out that investment in open work comes back; 

is there a way to "sign" gel images (maybe from the gel-doc itself?) so that manipulation is obvious?

an interesting thing is searchability. I often don't come back to notes because it's easier and more likely I'll get a relevant result by googling again! future lab notebook should have a live and very effective search.

Why do problems keep happening? Why do bugs which other people have hit keep recurring? Why does bad science even happen?
laser power supply troubles paper 

when you build a project, put aside a certain amount of money and time to justify helping future people 

At least with mathematics, it seems to generally be easier to find a starting point closer to your desired one than to work it out yourself. If you get stuck trying to massage things into a different representation, look harder for a different formulation.

\rule{\linewidth}{0.2pt}

In general, even though thesis works are generally pretty high quality, I don't find myself citing them very often. This might be because are packaged to be relevant when searched - breaking a large project with different components into a series of papers probably makes it more useful for later readers.

\rule{\linewidth}{0.2pt}

Peer review is pretty helpful. external input can dissuade you from the apparently frivolous but essential deviations that seem pretty helpful, but in general 

\rule{\linewidth}{0.2pt}

This was written in 4 parts: first, rough lab notes were made, then this was cleaned up into a long thesis-like document, and then this was compressed into the final paper. However, in that final compression step, a lot of "texture" and pedagogy was lost on the first draft, when writing as terse as possible. 

Don't worry about repeating yourself; duplicating sections in different contexts is fine.

\rule{\linewidth}{0.2pt}

Rather than focus effort on making marginal improvements to avoid errors in a certain technique, it may be better to put more effort to find a better experimental technique that is totally immune to these problems. Obviously this isn't always possible or practical.

\rule{\linewidth}{0.2pt}

Lesson learned: implementing safeties in hardware when possible, even in non-critical systems, can greatly speed development.

Like many microwave semiconductor HBT or pHEMT MMICs, the HMC996 amplifier requires careful biasing (discussed in section blah), or else it destroys itself. 

\rule{\linewidth}{0.2pt}

There is something of an over-arching lesson learned - maybe it's not actually good to learn this lesson, maybe it's more useful to assume, but...

It is interesting to think about the meta-issues surrounding this project. While an unusable \$600 Beta-Glo assay went flat, not a few kilometers away the food bank ran out of supplies and people were not able to feed their families. That is unjust. 

On the other hand, we have seen time and again that investment in science and technology - even basic research, so distant from the mechanics of society - can produce outsized effects on quality-of-life. Both NASA and CERN, neither of which do much related to people, produce 7-to-1 and 3-to-1 returns on investment. 

All of which will be a great comfort to the dead. 

You could fit a pandemic through a good-sized breakthrough. The vaccines are an excellent example. Moreover, on a personal level you learn new skills and techniques, to be more useful to others in the future.

So what went wrong here? 

Is it the avenue of investigation? An arrogance in decision making? Perhaps a lack of peer input. Maybe there were too few people involved - now that science is "bigger", we need bigger groups to efficiently manage it? 

Maybe if you don't have sufficient resources, equipment, knowledge, experience, or peers to persue something efficiently, or competently, and developing it slowly would not aid greatly in diffusing or disseminating knowledge, maybe it's not worth you pursuing it at all.

If a well-stocked lab and a few specialists could have banged this out in a week (which they could), was it worth it to bang this out in a year? Did anything actually go wrong, or is this just how it works?

It's interesting thoughts to toy with, but probably not a great idea to get wrapped up in this sort of self-pity and melancholic thinking. Or maybe it is. Who knows.

Doing the same thing that I was doing before - sitting in a basement, working on electronics. What are the odds that the thing that I was doing before was the right thing to do against a virus?

\rule{\linewidth}{0.2pt}

When to publish?

One the one hand, there're some pretty good reasons to want embargoes, like the Ingelfinger rules - no need to lather up a furor just for some idle musings, and publishing too early is a terrible idea. In retrospect, it was extremely good that I did not make a fuss about (or obtain funding for the original ) some extremely positive data; it turned out to be an embarrassing mistake in a data analysis script.

On the other hand, embargo rules came from publishers, and (like ) these decisions were probably somewhat motivated by financial considerations.

There's a recent movement towards more "live" and open science - it's hard to tell when the, especially in a pandemic. Fortunately, it's not like any of what we're discussing here actually matters, anyways.

\rule{\linewidth}{0.2pt}

This one was taught to me by Yuriy!

We were trying to write a pre-baked math worksheet into Wolfram Mathematica.

It is useful to first strictly implement a method precisely as written, and only when all parts are operational and understood, begin modifying for your own use.

This is common practice in many fields, but hadn't occurred to me for math. 

\rule{\linewidth}{0.2pt}

Indexes of papers compiled by government agencies, and gray literature in general, appear to be very useful.

\rule{\linewidth}{0.2pt}

Rigorous literature reviews are very important. de Seze has a good example: search terms are specified. If we had come across the paper by Bigior earlier, we may have

\rule{\linewidth}{0.2pt}

Papers only carry the scientific heritage that their authors saw fit to include in the references section, and only provide the context included in the "introduction". 

\rule{\linewidth}{0.2pt}

There seems to be a drive towards small volumes and microfluidics. This is great; these are cool technologies; but in our case these were a huge hindrance.

There are a lot of reasons why small volumes are useful: you can run more tests with a given quantity of sample - a 1500-well microplate assay would be a hard sell with even 1.5 mL tubes; small samples are diluted to a lesser degree. 

However, it should also be considered that most tolerances and precisions do not scale with volume. 
Rheology does not scale with volume, so bacterial culture becomes a challenge. Dust and contaminants do not scale. Optical path lengths are much shorter. Most assays will have decreased resolution. Precision in dispensing is much more critical, as is deformation due to autoclaving. The "hairs" that appear on machined polypropylene, which are almost impossible to remove, can be as large as your sample. Evaporation is much more critical.

Most importantly, annoyance scales inversely with size. It is hard to work with a quantity of fluid which is barely visible.

\rule{\linewidth}{0.2pt}

We often came across a situation in which minor errors in software,  would completely change the conclusion of our results.

Reproducible coding helps, but it would be much better if we had used standard software engineering best practices; red-teaming, unit testing on randomly generated data, etc. It might also be helpful if the data itself are blinded against randomly generated controls - in many cases that's not possible, but it might be useful in some circumstances.

See Phosphine.

It may be useful to make explicit to the reader where particular sensitivities - high gradients of conclusion against some factor - might exist in your research.

\rule{\linewidth}{0.2pt}

The phage field - and many other fields - seem to have a problem where most of the really important base discoveries related to practice - 

Some things actually seem to have been lost.

\rule{\linewidth}{0.2pt}

Writing a paper by writing the chapters and headings that you want, and then filling in the text, is quite hard. Just writing a big chunk of text, and then breaking that into many smaller sections, works a bit better.

\rule{\linewidth}{0.2pt}

It might be useful to watch file changes and autoreload. Practically every program in this project required the same three keystrokes to recompile; a recipe for RSI.

\rule{\linewidth}{0.2pt}

Automatic, no-effort documentation of simulation and experiment runs is critical.

It may be helpful to think of simulations very similarly to IRL experiments. 

A simulation is just a universe in a bottle that you can examine more closely; as with real-world, you can learn much from observation, but 

But this need for documentation conflicts with the rapid, iterative cycle necessary for productivity.

This is obvious to all competent, but when rapidly iteratively testing with simulations, it may be helpful to automatically save a package with images of all the components (schematics, graphs, input files) of each distinct test. 

For comparison to experiment, having a webcam take an image of the assembled board is also helpful. 

Many months of testing have vanished into the ether due to 

Version control alone isn't quite enough. Just having a simulation setup file somewhere in the commit history isn't "discoverable" - that is, you must be able to see what the input and output was without re-running the simulation. 

Manually taking notes tended to disrupt the flow of testing; and in any case, just noting "SIR filter has appropriate phase response" is almost useless. What {\it was} the phase response? Plot it, and upload it!

Software such as Sumatra, Sacred, recipy, and others. In our case, we used eLabFTW's elabapy bindings.

I think this is a good general rule: record as much detail as automatically as possible

\rule{\linewidth}{0.2pt}

It is far easier to use existing, well-characterized reference designs verbatim than to modify 

\rule{\linewidth}{0.2pt}

Memoization is more thoroughly considered in Scaling of Differential Equations with joblib.

Dill

When rapidly testing data analyses of simulations which aren't really conducive to unit testing, I previously used to run the whole simulation, look at the analysis, re-run the sim, etc.

This is slow. I often don't change the input parameters for the sim, but just the analysis. However, there's often a large amount of state to persist to disk, so it's not worth writing a serializer just to store this throwaway run.

In this case, saving the entire simulation session with 'dill' is very helpful.

\rule{\linewidth}{0.2pt}

Software opacity is evil.

\rule{\linewidth}{0.2pt}

A great deal of time was spent trying to resolve version conflicts and dependency hells with the numerous libraries used by all the simulation programs. Over a week was spent trying to recursively track down all the This also wastes developer time - some fraction of issues raised are due to library version conflicts. 

Packaged binaries help this slightly, but of course don't help if modifications are required, and managing shared libraries is still a tricky matter.

Good solutions include OpenFOAM's Docker installation. In some cases, using chroot with the original developer's Linux distribution is also of some utility.

But this all seems like quite a lot of overhead and opacity for what ultimately doesn't seem a super-complex problem: deterministically obtain a known-good version of a library, build locally, and set paths appropriately.

A good example might be gTest's cmake integration.

In the extreme, systems exist to extract every 

In some situations (especially where the library has a permissive licence) perhaps it could be useful to consider packaging a complete, batteries-included 'known good' repository, either with the source of all the correct library versions included, or with a script to clone and compile the specific version used, integrating all the libraries with the build system. 

For instance, this was done with the PDB reader in the OpenMM wrapper and JAMES.

Honestly, this might already account for a difference in productivity between, say, Python, and C++. the package manager.

\rule{\linewidth}{0.2pt}

There's also a very neat thing that seems to be common in computational biology, but which doesn't seem popular in other fields. After an algorithm or software tool is written (and the source published separately), a simple CGI frontend is written around it and hosted on the university's servers. eLNemo and the CHARMMing web interface are advanced examples of this. This way, anyone with an input file can get results without futzing around with installation, at least for the few decades that the servers are maintained.

The computational biologists have beat us at our own game.

\rule{\linewidth}{0.2pt}

We have always encountered wasting extreme amounts of time on subtle assembly mistakes in hardware prototypes. 

In one example in this project, many hours were wasted because the enamel insulation on a bodge wire had not burned off completely in a solder joint, leading to a high-impedance connection.

The same has occurred in previous projects; in one example, many days were spent debugging software to fix an apparently slow hardware interrupt, which ended up being the result of a poor solder paste stencil leading to a hidden high-impedance connection to a leadless package.

Many failures are the result of carelessness in modification and lack of inspection. Others would only have been found by a 100\% electrical test.

If flying-probe or bed-of-nails tests can be made sufficiently rapid and closely coupled with the existing toolchain, 

In {\it 2001: A space odyssey}, an automated system is shown guiding the troubleshooting of an assembly, apparently generating a fault tree of all the 

Boundary-scan features might really help 

\rule{\linewidth}{0.2pt}

Numerology doesn't pay

\rule{\linewidth}{0.2pt}

The ability to almost immediately compare simulation to experiment was of great use almost everywhere in this project. This hybrid, "lockstep" approach between theory, simulation, and practice works, I think, extremely well. Even if all these intermediate experiments fail, the mere process of setting up an experiment offers you insight - and forces you to persue leads - which would not otherwise have been gained. Is it better than, say, spending a year carefully establishing the theory behind an experiment, and then doing one? I'm not sure. Other teams have had great success with this.

\rule{\linewidth}{0.2pt}

This project started at the tail end of a project to produce ceramics. Many weeks were wasted; I had convinced myself that ceramics were required over FR4. 

\rule{\linewidth}{0.2pt}

I originally rationalized not contacting others about . There are some 10,000 labs working on a cure; it's not helpful to have random amateurs tying up expert time with ignorant flights of fancy. 

Later, as the project became more mature and seemed likely, this morphed into a sort of arrogance.

An expert in microwave engineering could probably have completed this entire project in a few days, rather than the months it took us.

\rule{\linewidth}{0.2pt}

\subsection{Hall of Hubris} \

Lest our hats stop fitting - a reminder that arrogance, fallacious beliefs, etc can creep in at any point

\rule{\linewidth}{0.2pt}

An inane remark:

\begin{displayquote}
We believe once we have the P. Syringae host, we from environmental samples
\end{displayquote}

Truly the depths of Dunning-Kruger.

\rule{\linewidth}{0.2pt}

Sometimes vertical integration is the wrong move. Objectively, in this case, it was simply the *wrong decision*. 

\rule{\linewidth}{0.2pt}

An expert and distinguished gentleman that we contacted regarding assistance resolving transients in our microstrip VCO stated the following:

This was a perfectly sensible remark; it is almost always the case that (at X-band, no less!) a custom IC would have been needed to build a VCO.

Also, if taken in the context of a tired, overworked PI getting an unsolicited email from an excessively verbose undergraduate at a different university, I hardly think I would have replied differently.

However, I think this person may have missed out. Learning 

So perhaps it is wise to ponder the ideas of fools for skeet; one always learns target practice, if only an example what not to do, and occasionally one learns positively. I have often found that I learn greatly from working on the projects of others.

We present this only as a cautionary tale in the hopes that someday I will listen.

 This is 

but, some months later, it was found that he was *right* - absolutely right. This was a grave error in management!

\rule{\linewidth}{0.2pt}

Photomultiplier

"Does anyone know of a circuit that can discriminate color PMT"?

only works if scintillator

%\end{multicols}

\end{document}

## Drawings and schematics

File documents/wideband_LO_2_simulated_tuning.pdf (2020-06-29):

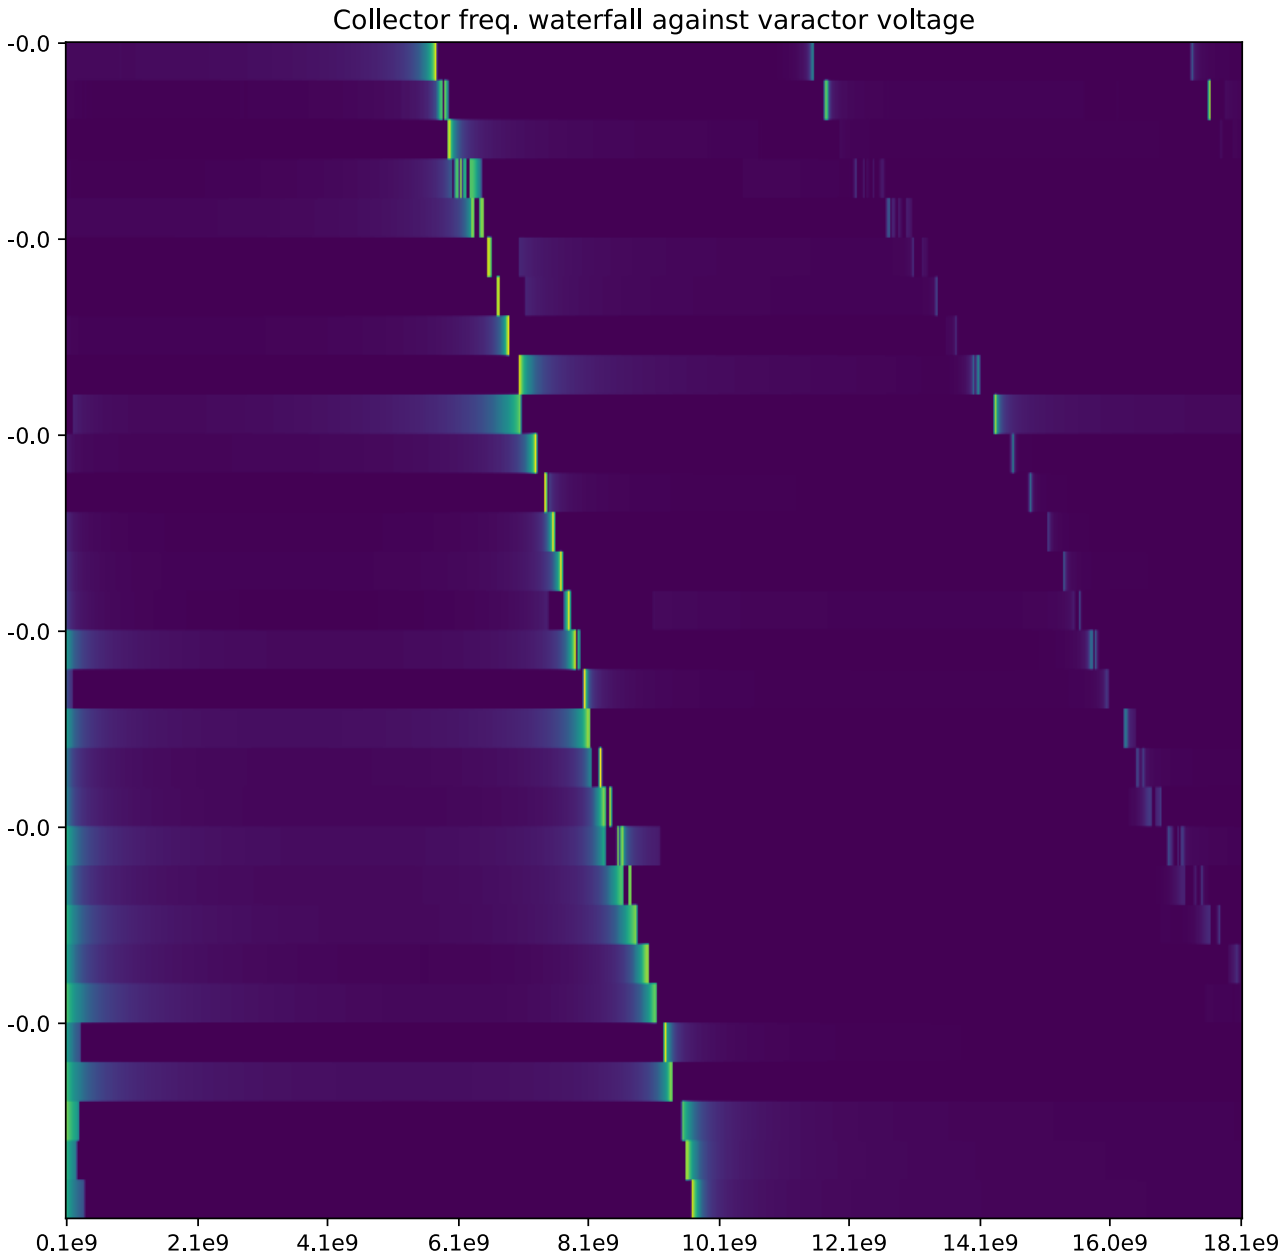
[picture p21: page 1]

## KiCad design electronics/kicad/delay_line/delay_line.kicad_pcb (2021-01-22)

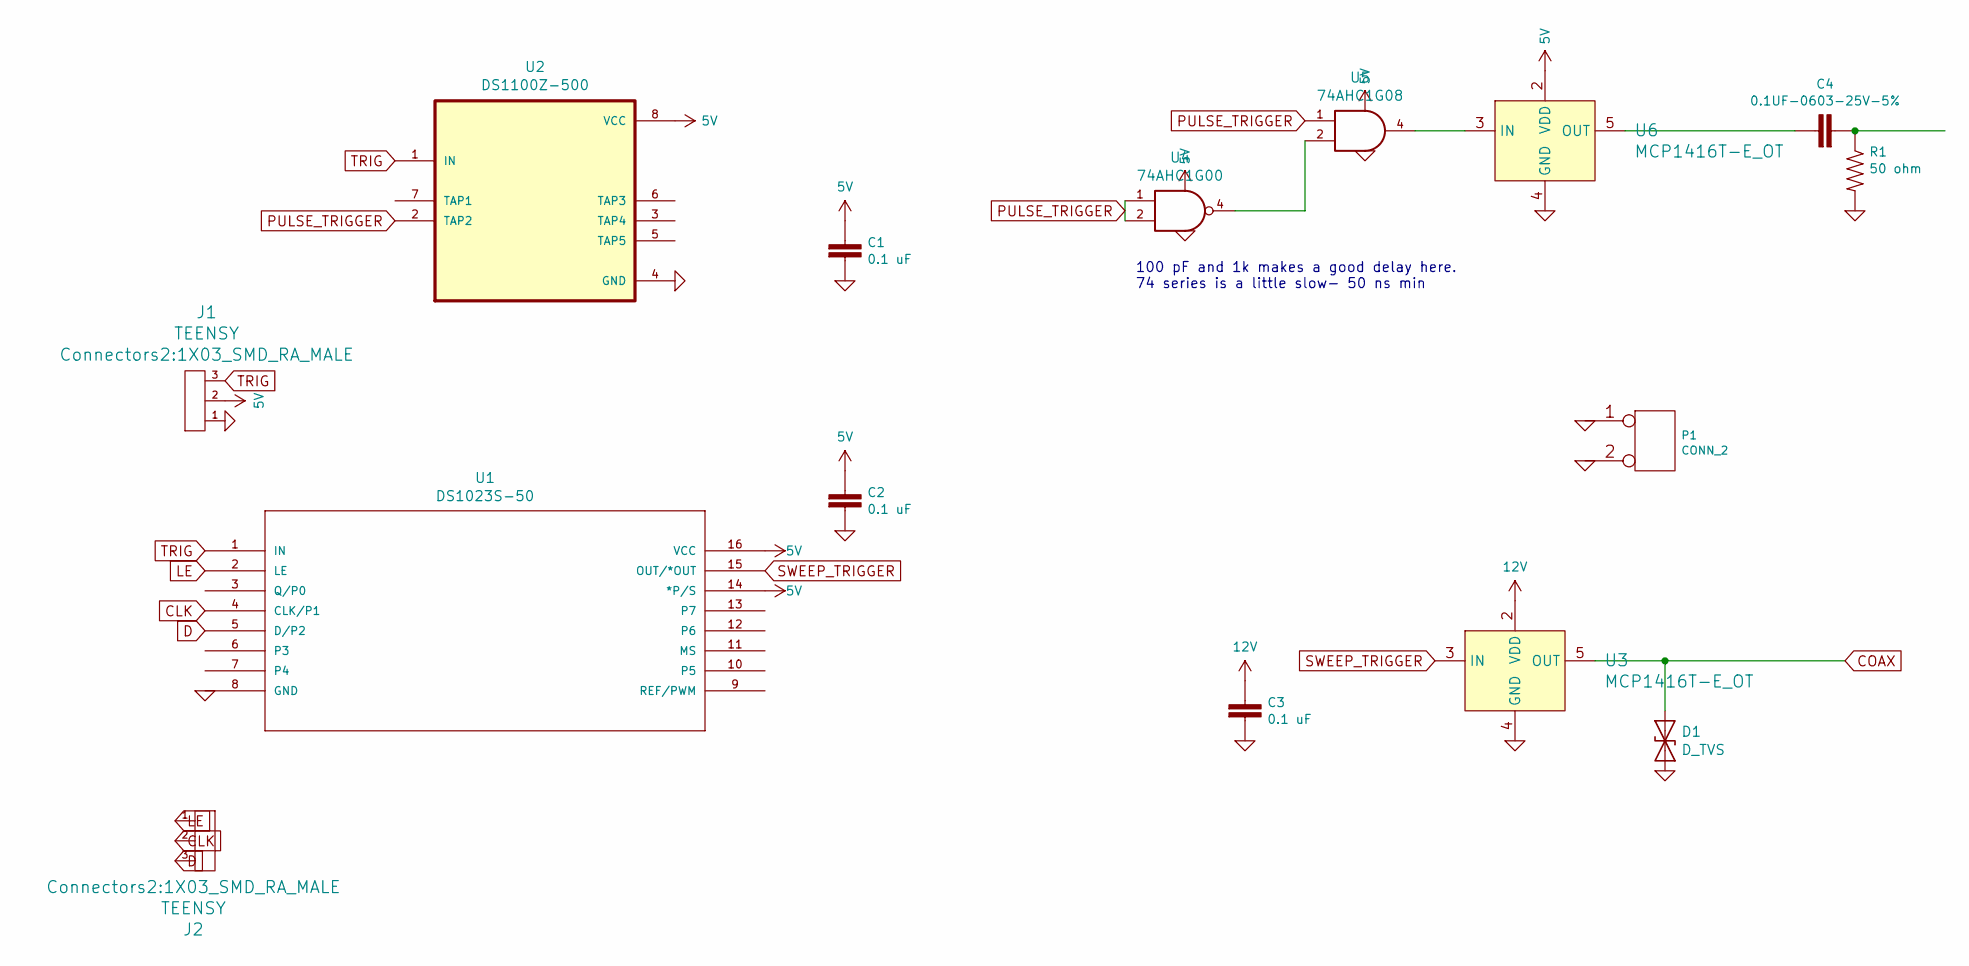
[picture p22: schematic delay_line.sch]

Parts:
C1, C2, C3: 0.1 uF; C_0603_1608Metric
C4: 0.1UF-0603-25V-5%; 0603
D1: D_TVS; D_SMA
J1, J2: TEENSY; 1X03_SMD_RA_MALE
P1: CONN_2; JUMPER_5102
R1: 50 ohm; 0805
U1: DS1023S-50; SOIC-16W_7.5x10.3mm_P1.27mm; MANUFACTURER_PART_NUMBER DS1023S50+
U2: DS1100Z-500; SOIC-8_3.9x4.9mm_P1.27mm
U3, U6: MCP1416T-E_OT; SOT-753; MPN MCP1416T-E/OT; Digi-Key_PN MCP1416T-E/OTCT-ND
U4: 74AHC1G00; SOT-23-5
U5: 74AHC1G08; SOT-23-5

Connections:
5V: C1.1, C2.1, J1.2, U1.14 (*P/S), U1.16 (VCC), U2.8 (VCC), U4.5 (VCC), U5.5 (VCC), U6.2 (VDD)
12V: C3.1, U3.2 (VDD)
CLK: J2.2, U1.4 (CLK/P1)
COAX: D1.1 (A1), U3.5 (OUT)
D: J2.3, U1.5 (D/P2)
GND: C1.2, C2.2, C3.2, D1.2 (A2), J1.1, P1.1, P1.2 (PM), R1.2, U1.8 (GND), U2.4 (GND), U3.4 (GND), U4.3 (GND), U5.3 (GND), U6.4 (GND)
LE: J2.1, U1.2 (LE)
unnamed: C4.1, U6.5 (OUT)
unnamed: C4.2, R1.1
unnamed: U4.4, U5.2
unnamed: U5.4, U6.3 (IN)
PULSE_TRIGGER: U2.2 (TAP2), U4.1, U4.2, U5.1
SWEEP_TRIGGER: U1.15 (OUT/*OUT), U3.3 (IN)
TRIG: J1.3, U1.1 (IN), U2.1 (IN)

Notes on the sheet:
100 pF and 1k makes a good delay here. 74 series is a little slow- 50 ns min

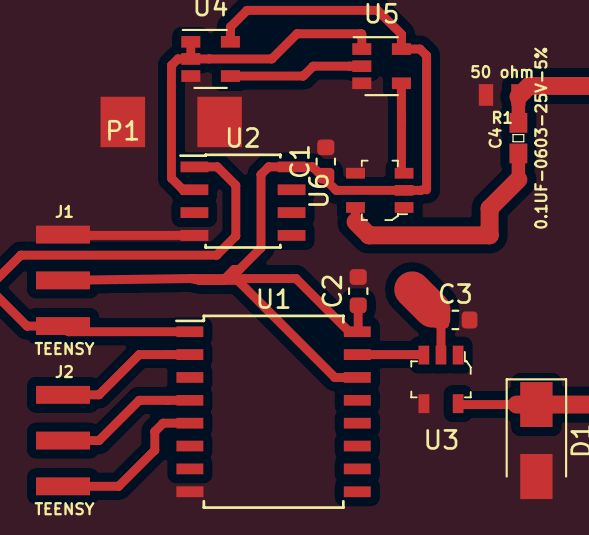
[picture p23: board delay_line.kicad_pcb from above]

Board: 2 copper layers, 15 parts (0 on the bottom side), 14 nets.

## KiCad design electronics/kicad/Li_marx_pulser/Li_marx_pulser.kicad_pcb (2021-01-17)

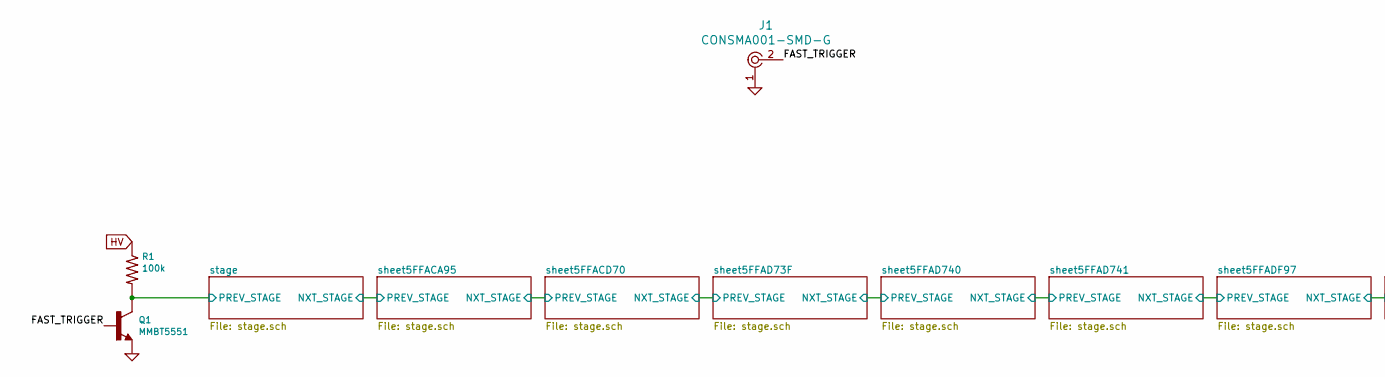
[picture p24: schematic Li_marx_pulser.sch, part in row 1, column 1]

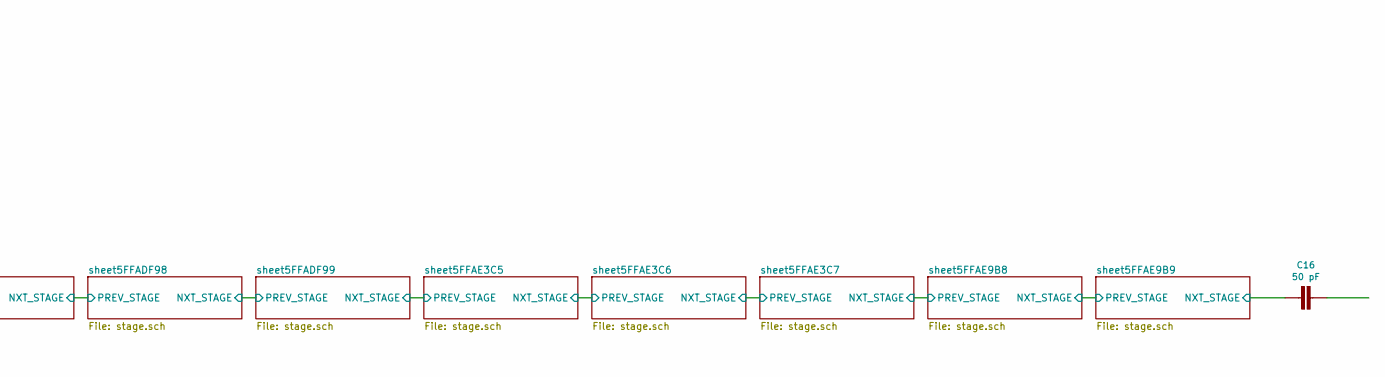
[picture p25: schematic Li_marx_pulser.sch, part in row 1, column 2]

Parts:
C16: 50 pF; 1206
J1: CONSMA001-SMD-G; RF_SMA_Receptical_Vertical_CONSMA001-SMD-G; MPN CONSMA001-SMD-G; Digi-Key_PN CONSMA001-SMD-G-ND
Q1: MMBT5551; SOT23-3
R1: 100k; R_2512_6332Metric

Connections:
/FAST_TRIGGER: J1.2, Q1.1 (B)
/sheet5FFAE9B9/NXT_STAGE: C16.2; also elsewhere on the board
/stage/PREV_STAGE: Q1.3 (C), R1.2; also elsewhere on the board
GND: J1.1, Q1.2 (E); also elsewhere on the board
HV: R1.1; also elsewhere on the board

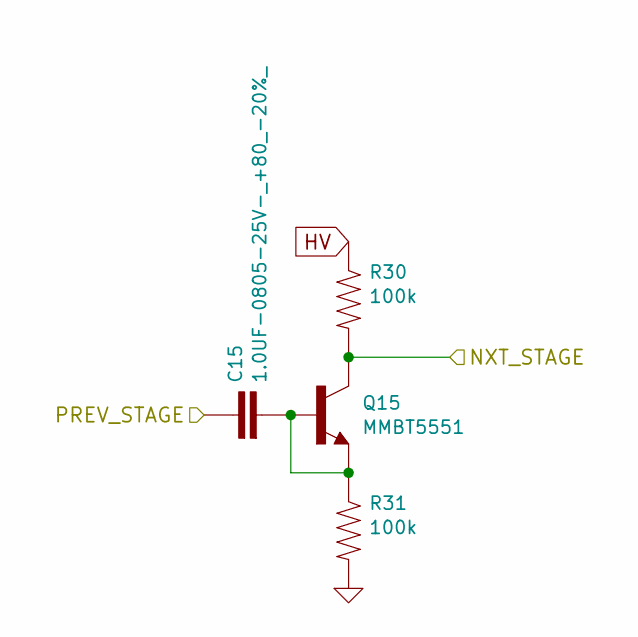
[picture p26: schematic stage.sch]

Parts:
C2: 1.0UF-0805-25V-_+80_-20%_; 1111(2828)
Q2: MMBT5551; SOT23-3
R4, R5: 100k; R_2512_6332Metric

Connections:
/stage/NXT_STAGE: Q2.3 (C), R4.2; also elsewhere on the board
/stage/PREV_STAGE: C2.1; also elsewhere on the board
GND: R5.2; also elsewhere on the board
HV: R4.1; also elsewhere on the board
unnamed: C2.2, Q2.1 (B), Q2.2 (E), R5.1

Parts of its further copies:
C3, C4, C5, C6, C7, C8, C9, C10, C11, C12, C13, C14, C15: 1.0UF-0805-25V-_+80_-20%_; 1111(2828)
Q3, Q4, Q5, Q6, Q7, Q8, Q9, Q10, Q11, Q12, Q13, Q14, Q15: MMBT5551; SOT23-3
R6, R7, R8, R9, R10, R11, R12, R13, R14, R15, R16, R17, R18, R19, R20, R21, R22, R23, R24, R25, R26, R27, R28, R29, R30, R31: 100k; R_2512_6332Metric

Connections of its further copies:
/sheet5FFACA95/NXT_STAGE: C4.1, Q3.3 (C), R6.2
/sheet5FFACD70/NXT_STAGE: C5.1, Q4.3 (C), R8.2
/sheet5FFAD73F/NXT_STAGE: C6.1, Q5.3 (C), R10.2
/sheet5FFAD740/NXT_STAGE: C7.1, Q6.3 (C), R12.2
/sheet5FFAD741/NXT_STAGE: C8.1, Q7.3 (C), R14.2
/sheet5FFADF97/NXT_STAGE: C9.1, Q8.3 (C), R16.2
/sheet5FFADF98/NXT_STAGE: C10.1, Q9.3 (C), R18.2
/sheet5FFADF99/NXT_STAGE: C11.1, Q10.3 (C), R20.2
/sheet5FFAE3C5/NXT_STAGE: C12.1, Q11.3 (C), R22.2
/sheet5FFAE3C6/NXT_STAGE: C13.1, Q12.3 (C), R24.2
/sheet5FFAE3C7/NXT_STAGE: C14.1, Q13.3 (C), R26.2
/sheet5FFAE9B8/NXT_STAGE: C15.1, Q14.3 (C), R28.2
/sheet5FFAE9B9/NXT_STAGE: Q15.3 (C), R30.2; also elsewhere on the board
/stage/NXT_STAGE: C3.1; also elsewhere on the board
GND: R7.2, R9.2, R11.2, R13.2, R15.2, R17.2, R19.2, R21.2, R23.2, R25.2, R27.2, R29.2, R31.2; also elsewhere on the board
HV: R6.1, R8.1, R10.1, R12.1, R14.1, R16.1, R18.1, R20.1, R22.1, R24.1, R26.1, R28.1, R30.1; also elsewhere on the board
unnamed: C3.2, Q3.1 (B), Q3.2 (E), R7.1
unnamed: C4.2, Q4.1 (B), Q4.2 (E), R9.1
unnamed: C5.2, Q5.1 (B), Q5.2 (E), R11.1
unnamed: C6.2, Q6.1 (B), Q6.2 (E), R13.1
unnamed: C7.2, Q7.1 (B), Q7.2 (E), R15.1
unnamed: C8.2, Q8.1 (B), Q8.2 (E), R17.1
unnamed: C9.2, Q9.1 (B), Q9.2 (E), R19.1
unnamed: C10.2, Q10.1 (B), Q10.2 (E), R21.1
unnamed: C11.2, Q11.1 (B), Q11.2 (E), R23.1
unnamed: C12.2, Q12.1 (B), Q12.2 (E), R25.1
unnamed: C13.2, Q13.1 (B), Q13.2 (E), R27.1
unnamed: C14.2, Q14.1 (B), Q14.2 (E), R29.1
unnamed: C15.2, Q15.1 (B), Q15.2 (E), R31.1

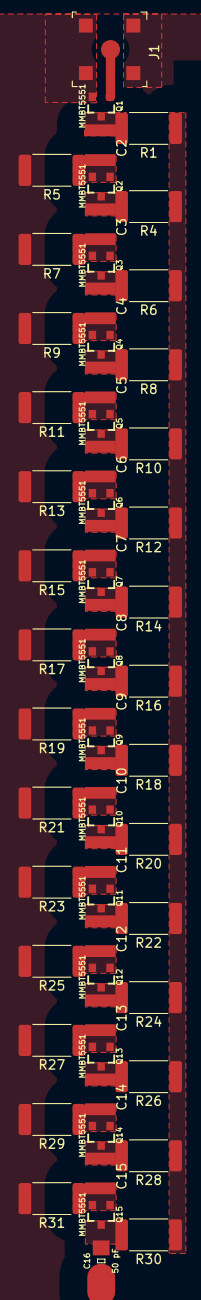
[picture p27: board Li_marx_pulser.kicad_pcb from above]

Board: 2 copper layers, 60 parts (0 on the bottom side), 32 nets.

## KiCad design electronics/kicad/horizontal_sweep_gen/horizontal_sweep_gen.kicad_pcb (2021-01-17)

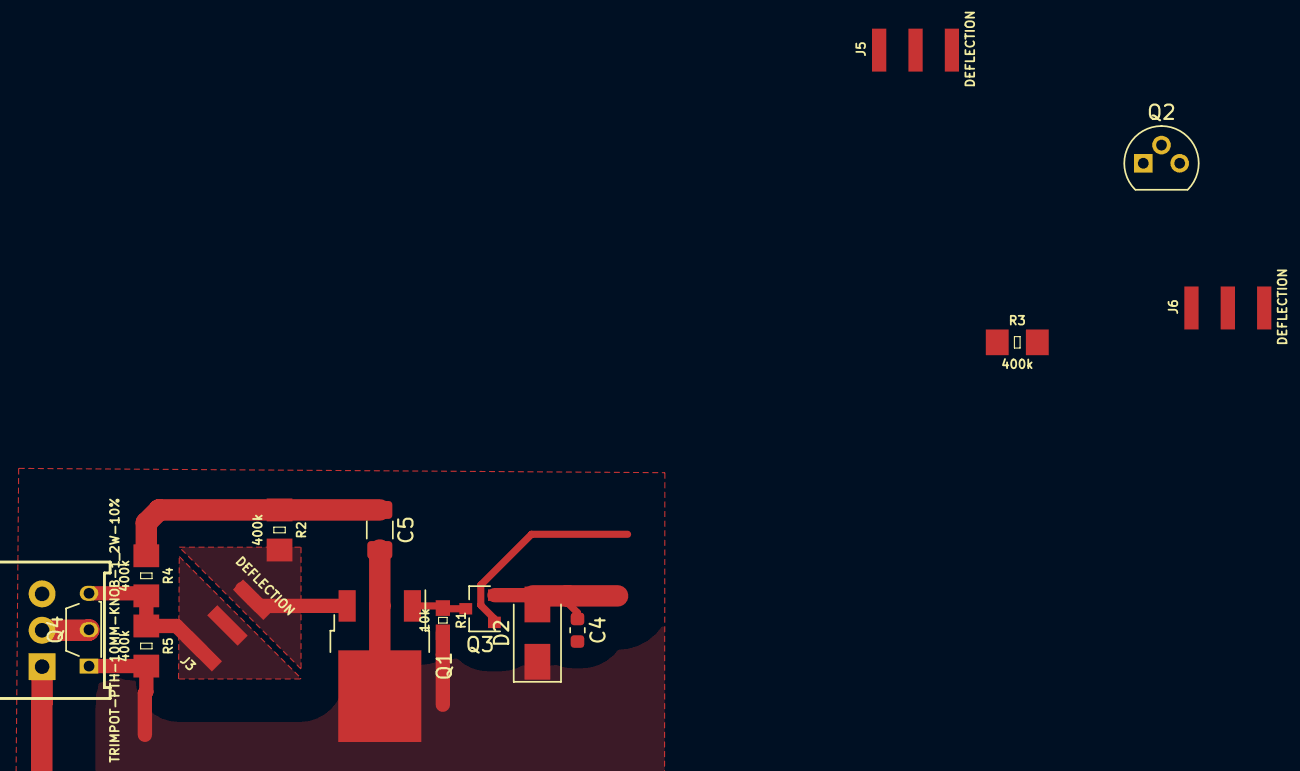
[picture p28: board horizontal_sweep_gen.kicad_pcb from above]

Board: 2 copper layers, 16 parts (0 on the bottom side), 8 nets.

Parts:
C4: 0.1 uF; C_0603_1608Metric
C5: 50 pF; C_1206_3216Metric
D2: D_TVS; D_SMA
J3, J5, J6: DEFLECTION; 1X03_SMD_RA_MALE
Q1: TSM2N100CHC5G; TO-252-3_TabPin2
Q2: ZTX458; TO-92
Q3: BSS84; SOT-23
Q4: ZTX458; TO-92S_Wide
R1: 10k; 0603
R2, R3, R4, R5: 400k; 1206
VR1: TRIMPOT-PTH-10MM-KNOB-1_2W-10%; TRIMPOT-PTH-3386U

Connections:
GND: C4.2, C5.2, D2.1, Q1.2, Q2.1, Q4.1, R1.2, R5.2
HV: C5.1, R2.1, R4.1
HV_CENTER: J3.1, J3.2, Q4.3, R4.2, R5.1
unnamed: J5.1, Q2.3, R3.2
unnamed: Q1.1, Q3.3, R1.1
unnamed: Q4.2, VR1.2
SWEEP: J3.3, Q1.3, R2.2
VSWEEP_SLOPE: C4.1, D2.2, J6.1, Q3.2

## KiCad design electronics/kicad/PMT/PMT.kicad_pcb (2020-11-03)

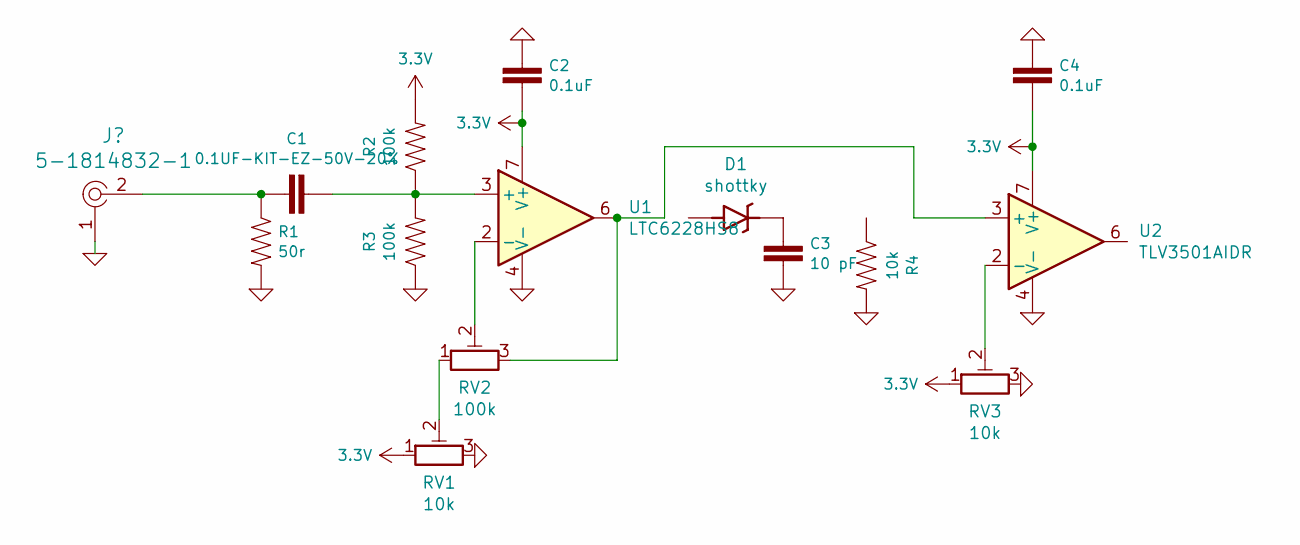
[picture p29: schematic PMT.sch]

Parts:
C1: 0.1UF-KIT-EZ-50V-20%; CAP-PTH-SMALL-KIT
C2, C4: 0.1uF; CAP-PTH-SMALL-KIT
C3: 10 pF; CAP-PTH-SMALL-KIT
D1: shottky; SMA-DIODE
R1: 50r; AXIAL-0.3
R2, R3: 100k; AXIAL-0.3
R4: 10k; AXIAL-0.3
RV1, RV3: 10k; PinHeader_1x03_P2.54mm_Vertical
RV2: 100k; PinHeader_1x03_P2.54mm_Vertical
U1: LTC6228HS8; DIP-8_W7.62mm
U2: TLV3501AIDR; DIP-8_W7.62mm

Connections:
3.3V: C2.2, C4.2, R2.P$2 (2), RV1.1, RV3.1, U1.7 (V+), U2.7 (V+)
GND: C2.1, C3.2, C4.1, R1.P$2 (2), R3.P$1 (1), R4.P$2 (2), RV1.3, RV3.3, U1.4 (V-), U2.4 (V-); also elsewhere on the board
unnamed: C1.1, R2.P$1 (1), R3.P$2 (2), U1.3 (+)
unnamed 3: C1.2, R1.P$1 (1); also elsewhere on the board
unnamed: C3.1, D1.C
unnamed: RV1.2, RV2.1
unnamed: RV2.2, U1.2 (-)
unnamed: RV2.3, U1.6, U2.3 (+)
unnamed: RV3.2, U2.2 (-)

Board: 2 copper layers, 15 parts (0 on the bottom side), 9 nets, no tracks yet.

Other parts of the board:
J1: 5-1814832-1; RF_SMA_Vertical_5-1814832-1

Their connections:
GND: J1.1; also elsewhere on the board
unnamed 3: J1.2; also elsewhere on the board

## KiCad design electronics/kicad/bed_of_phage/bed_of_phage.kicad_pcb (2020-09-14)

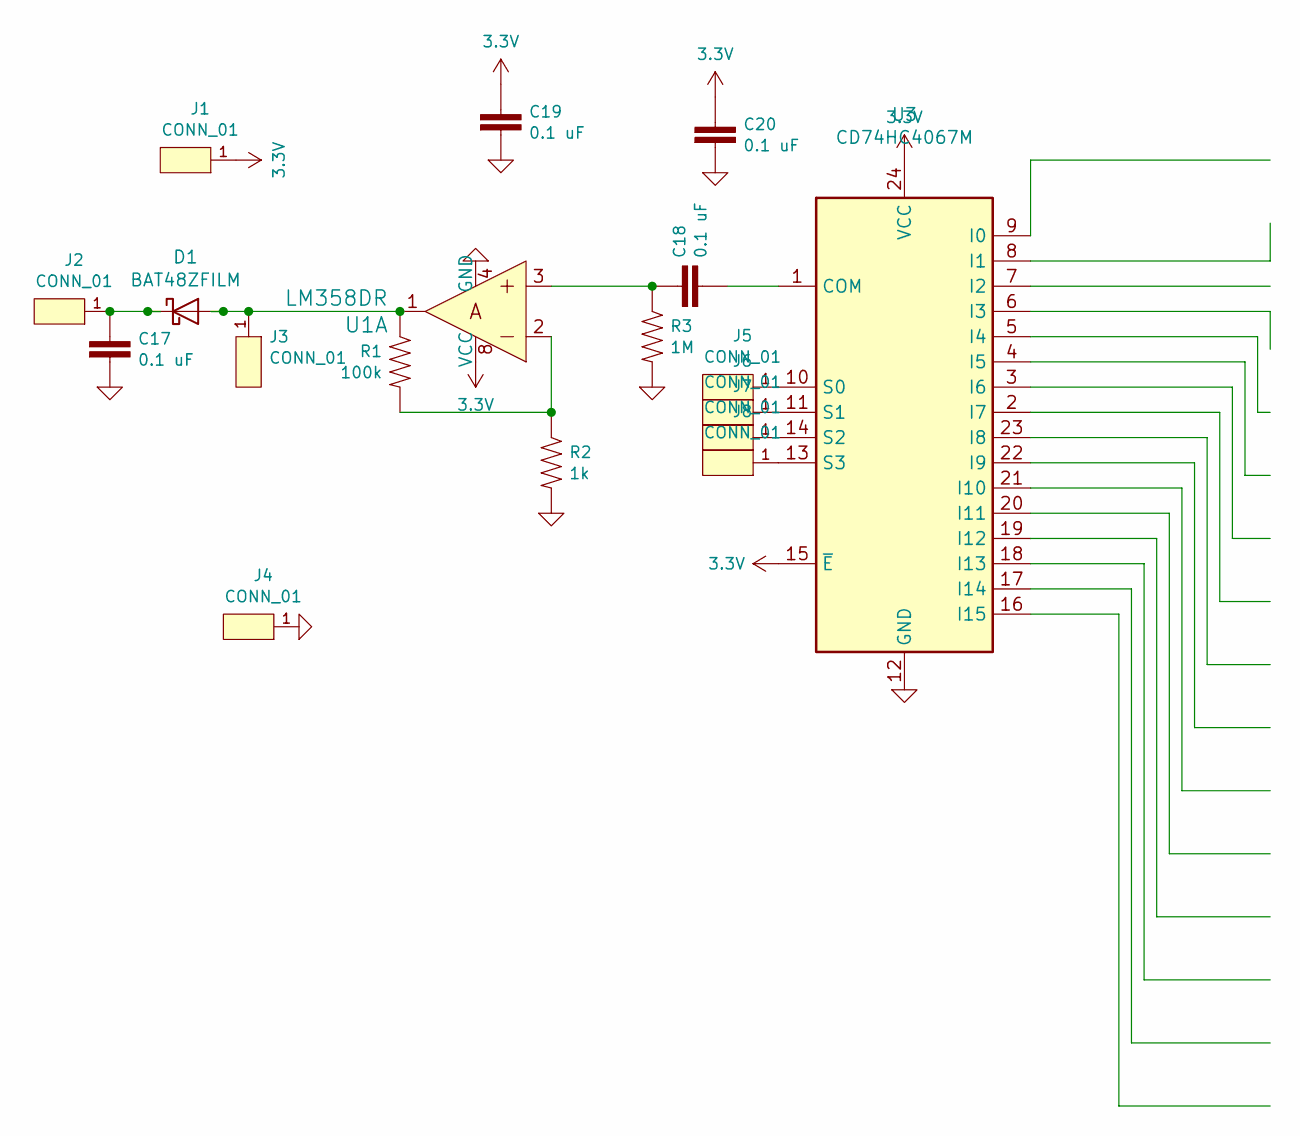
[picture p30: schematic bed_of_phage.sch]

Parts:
C17, C18, C19, C20: 0.1 uF; 0603
D1: BAT48ZFILM; D_SOD-123
J1, J2, J3, J4, J5, J6, J7, J8: CONN_01; 1X01
R1: 100k; 0603
R2: 1k; 0603
R3: 1M; 0603
U1: LM358DR; SOIC-8_W3.9mm; MPN LM358DR; Digi-Key_PN 296-1014-1-ND
U3: CD74HC4067M; SOIC-24W_7.5x15.4mm_P1.27mm

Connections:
3.3V: C19.1, C20.1, J1.1, U1.8 (VCC), U3.15 (~E), U3.24 (VCC)
GND: C17.2, C19.2, C20.2, J4.1, R2.2, R3.2, U1.4 (GND), U3.12 (GND)
unnamed: C17.1, D1.1 (K), J2.1
unnamed: C18.1, R3.1, U1.3
unnamed: C18.2, U3.1 (COM)
unnamed: D1.2 (A), J3.1, R1.1, U1.1
unnamed: J5.1, U3.10 (S0)
unnamed: J6.1, U3.11 (S1)
unnamed: J7.1, U3.14 (S2)
unnamed: J8.1, U3.13 (S3)
unnamed: R1.2, R2.1, U1.2

Board: 2 copper layers, 18 parts (0 on the bottom side), 11 nets, no tracks yet.

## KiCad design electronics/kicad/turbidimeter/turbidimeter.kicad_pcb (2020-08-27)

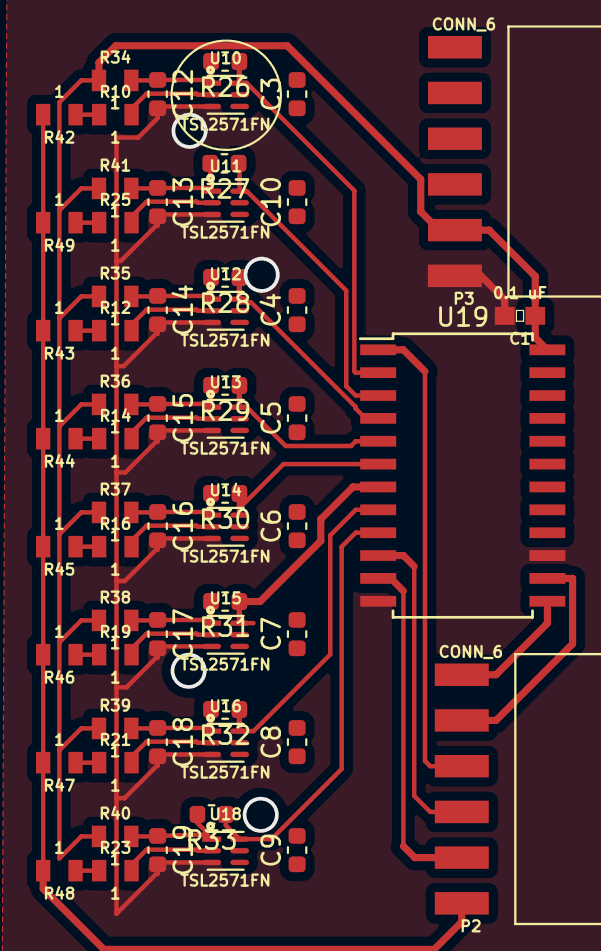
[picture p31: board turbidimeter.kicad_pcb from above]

Board: 2 copper layers, 60 parts (0 on the bottom side), 40 nets.

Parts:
C1: 0.1 uF; 0603
C3, C4, C5, C6, C7, C8, C9, C10, C12, C13, C14, C15, C16, C17, C18, C19: 0.1 uF; C_0603_1608Metric
P2, P3: CONN_6; 1X06-SMD-FEMALE
R10, R12, R14, R16, R19, R21, R23, R25, R34, R35, R36, R37, R38, R39, R40, R41, R42, R43, R44, R45, R46, R47, R48, R49: 1; 0805
R26, R27, R28, R29, R30, R31, R32, R33: 10k; R_0603_1608Metric
U10, U11, U12, U13, U14, U15, U16, U18: TSL2571FN; DFN-6-2X2
U19: CD74HC4067M; SOIC-24W_7.5x15.4mm_P1.27mm

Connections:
3.3V: C1.1, P3.5, R34.1, R35.1, R36.1, R37.1, R38.1, R39.1, R40.1, R41.1, U19.24
/S0: R33.1, U18.6, U19.9
/S1: R32.1, U16.6, U19.8
/S2: R31.1, U15.6, U19.7
/S3: R30.1, U14.6, U19.6
/S4: R29.1, U13.6, U19.5
/S5: R28.1, U12.6, U19.4
/S6: R27.1, U11.6, U19.3
/S7: R26.1, U10.6, U19.2
A0: P2.5, U19.11
A1: P2.4, U19.10
A2: P2.2, U19.14
A3: P2.1, U19.13
GND: C1.2, C12.2, C13.2, C14.2, C15.2, C16.2, C17.2, C18.2, C19.2, P3.6, U10.3, U11.3, U12.3, U13.3, U14.3, U15.3, U16.3, U18.3, U19.12, U19.15
unnamed: C12.1, R26.2, R34.2, U10.1
unnamed: C13.1, R27.2, R41.2, U11.1
unnamed: C14.1, R28.2, R35.2, U12.1
unnamed: C15.1, R29.2, R36.2, U13.1
unnamed: C16.1, R30.2, R37.2, U14.1
unnamed: C17.1, R31.2, R38.2, U15.1
unnamed: C18.1, R32.2, R39.2, U16.1
unnamed: C19.1, R33.2, R40.2, U18.1
unnamed: R10.1, R42.1
unnamed: R10.2, U10.2
unnamed: R12.1, R43.1
unnamed: R12.2, U12.2
unnamed: R14.1, R44.1
unnamed: R14.2, U13.2
unnamed: R16.1, R45.1
unnamed: R16.2, U14.2
unnamed: R19.1, R46.1
unnamed: R19.2, U15.2
unnamed: R21.1, R47.1
unnamed: R21.2, U16.2
unnamed: R23.1, R48.1
unnamed: R23.2, U18.2
unnamed: R25.1, R49.1
unnamed: R25.2, U11.2
SCL: P2.6, R42.2, R43.2, R44.2, R45.2, R46.2, R47.2, R48.2, R49.2
SDA: P2.3, U19.1

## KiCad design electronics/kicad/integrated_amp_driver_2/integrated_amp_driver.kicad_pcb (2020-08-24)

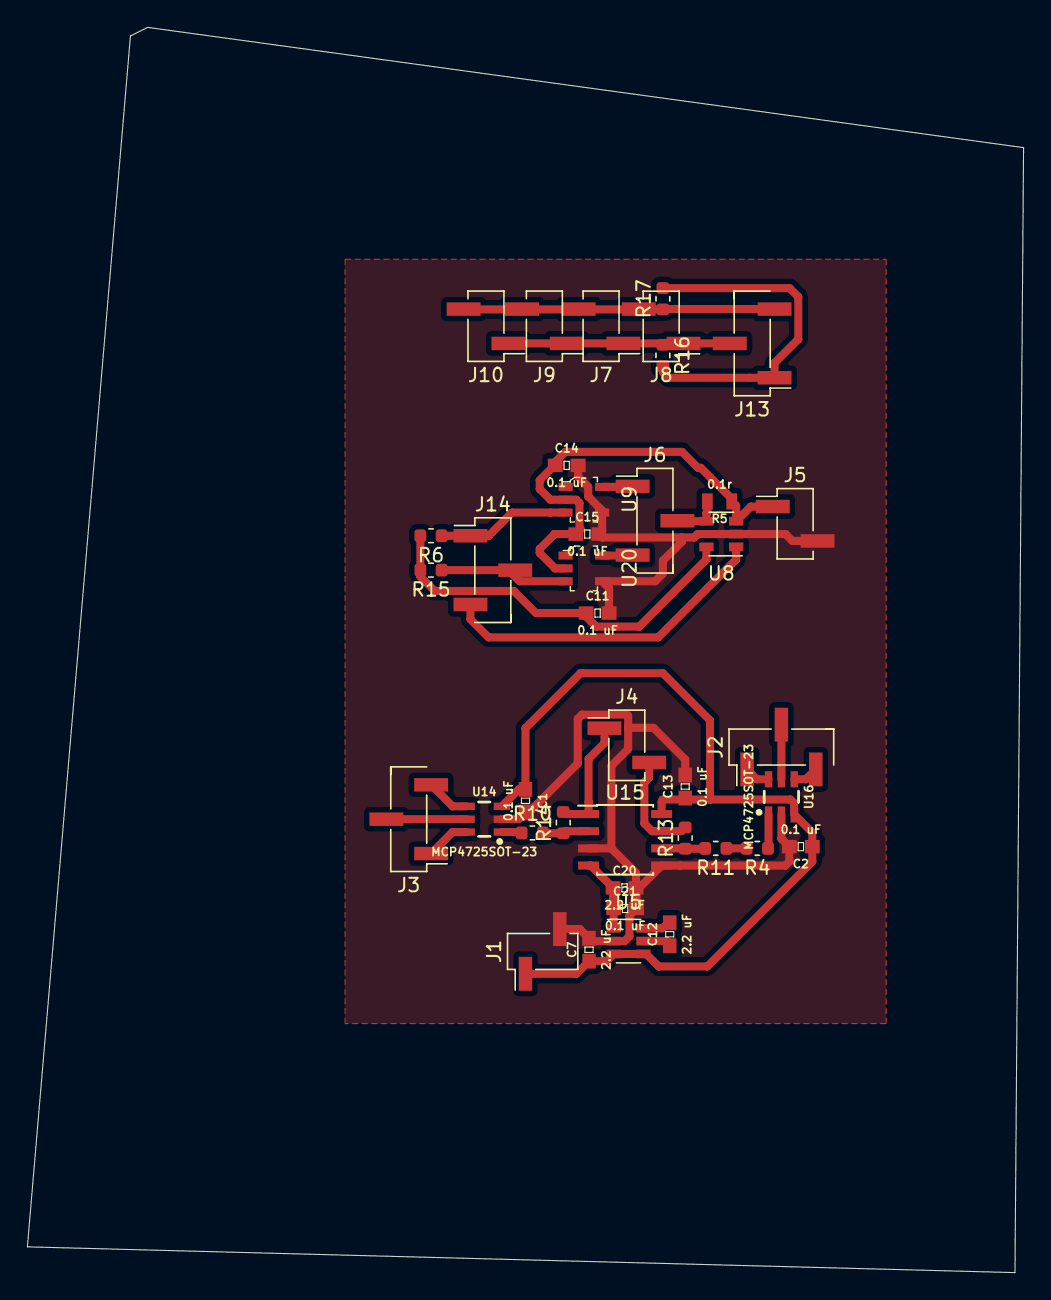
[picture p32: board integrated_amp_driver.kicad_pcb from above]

Board: 2 copper layers, 73.7 x 92.1 mm, 39 parts (0 on the bottom side), 23 nets.

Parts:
C1, C2, C11, C13, C14, C15, C21: 0.1 uF; 0603
C7, C12, C20: 2.2 uF; 0603
J1, J4, J5, J7, J8, J9, J10: CONN_02; PinHeader_1x02_P2.54mm_Vertical_SMD_Pin1Left
J2, J3, J6, J13, J14: CONN_02; PinHeader_1x03_P2.54mm_Vertical_SMD_Pin1Left
R4, R6, R10, R11, R13, R14, R15: 1k; R_0603_1608Metric
R5: 0.1r; 0805
R16, R17: 4.7k; R_0603_1608Metric
U5: LM2776; SOT-23-6
U8: INA194; SOT-23-5
U9, U20: MCP1416T-E_OT; SOT-753
U14, U16: MCP4725SOT-23; SOT23-6
U15: TS912IDT; SOIC-8_3.9x4.9mm_P1.27mm

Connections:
3.3V: C11.1, J13.1, R6.2, R15.2, R16.2, R17.2, U8.5
5V: C1.1, C2.1, C7.1, C13.1, C14.1, C15.1, J1.1, J5.1, R5.1, U5.3, U5.4, U8.3, U9.2, U14.3, U15.8, U16.3, U20.2
-5V: C20.1, C21.1, U5.1, U15.4
AMP_DRAIN_CONTROL_: J6.3, U20.5
AMP_DRAIN_SUPPLY: J6.2, R5.2, U8.4
AMP_GAIN_CONTROL_: J4.1, R14.2, U15.1
AMP_GATE_CONTROL_: J4.2, R13.2, U15.7
GAIN_DAC_I2C_SELECT: J3.1, U14.6
GATE_DAC_I2C_SELECT: J2.1, U16.6
GND: C1.2, C2.2, C7.2, C11.2, C13.2, C14.2, C15.2, C20.2, C21.2, J1.2, J5.2, U5.2, U8.2, U9.4, U14.2, U15.3, U15.5, U16.2, U20.4
unnamed: C12.1, U5.5
unnamed: C12.2, U5.6
unnamed: R4.1, U16.1
unnamed: R10.1, U14.1
unnamed: R10.2, R14.1, U15.2
unnamed: R4.2, R11.1
unnamed: R11.2, R13.1, U15.6
SCL: J2.2, J3.2, J7.1, J8.1, J9.1, J10.1, J13.2, R16.1, U14.5, U16.5
SDA: J2.3, J3.3, J7.2, J8.2, J9.2, J10.2, J13.3, R17.1, U14.4, U16.4
VCO_POWER_CONTROL_: J6.1, U9.5
current_sense_output: J14.3, U8.1
~AMP_DRAIN_CONTROL: J14.2, R15.1, U20.3
~VCO_POWER_CONTROL: J14.1, R6.1, U9.3

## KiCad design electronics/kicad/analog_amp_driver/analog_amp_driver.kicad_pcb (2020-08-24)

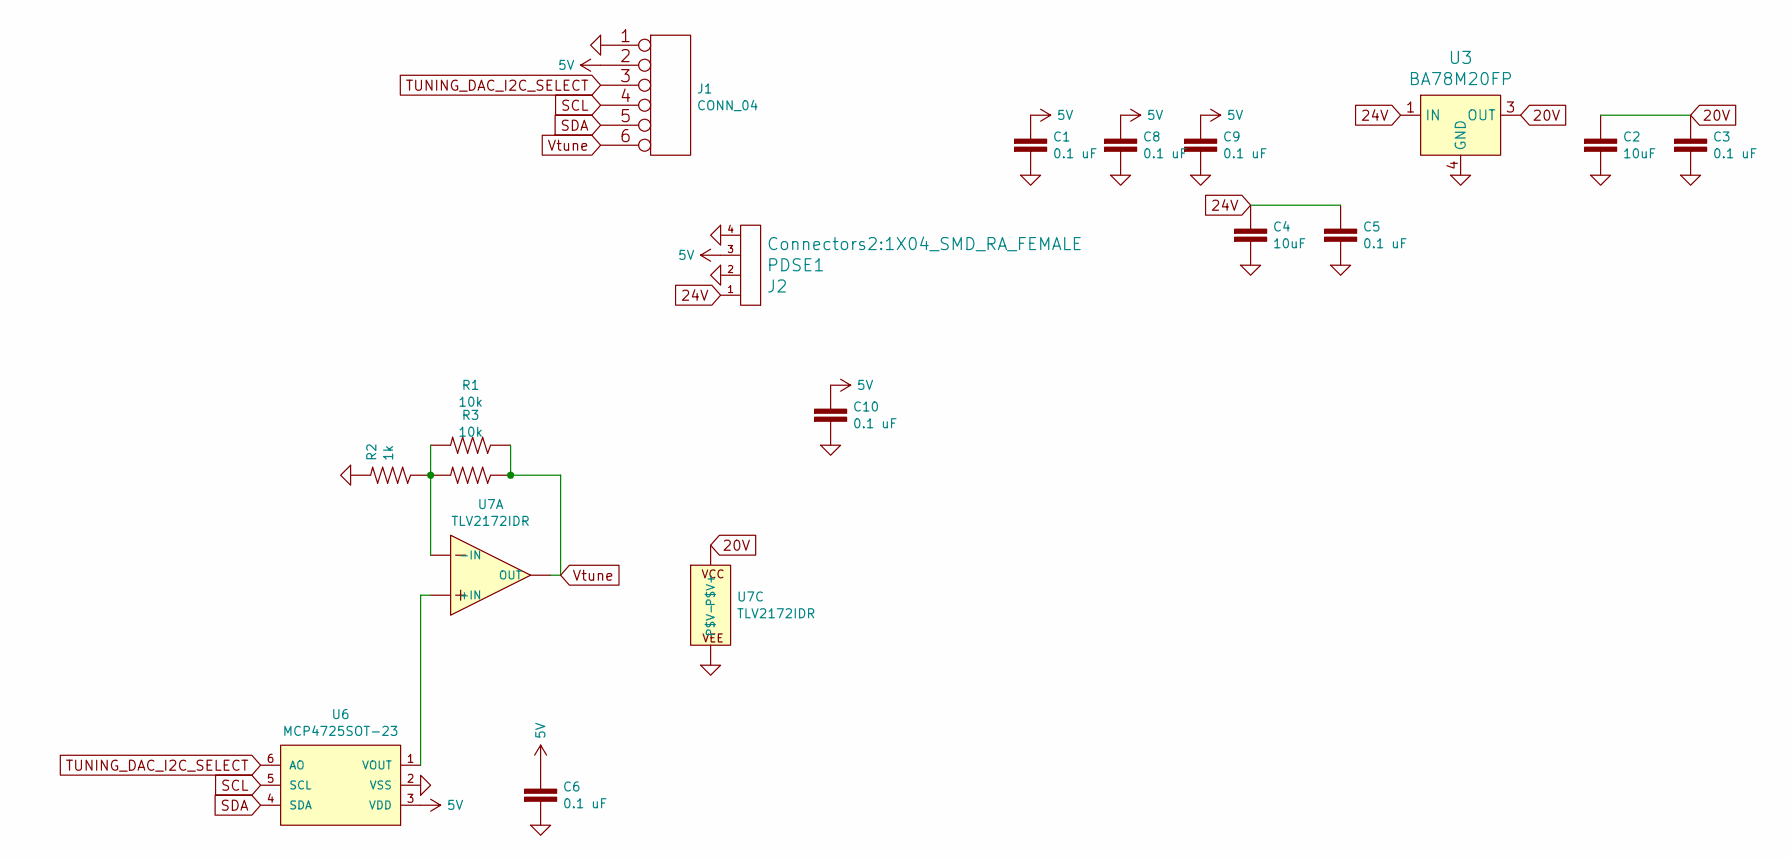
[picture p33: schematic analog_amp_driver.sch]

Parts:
C1, C3, C5, C6, C8, C9, C10: 0.1 uF; 0603
C2, C4: 10uF; 1206
J1: CONN_04; 1X06-SMD-FEMALE
J2: PDSE1; 1X04_SMD_RA_FEMALE
R1, R3: 10k; R_0603_1608Metric
R2: 1k; R_0603_1608Metric
U3: BA78M20FP; TO-252-3; MPN MC7805BDTRKG; Digi-Key_PN MC7805BDTRKGOSCT-ND
U6: MCP4725SOT-23; SOT23-6
U7: TLV2172IDR; SOIC-8_3.9x4.9mm_P1.27mm

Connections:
5V: C1.1, C6.1, C8.1, C9.1, C10.1, J1.2, J2.3, U6.3 (VDD)
20V: C2.1, C3.1, U3.3 (OUT), U7.8 (P$V+)
24V: C4.1, C5.1, J2.1, U3.1 (IN)
GND: C1.2, C2.2, C3.2, C4.2, C5.2, C6.2, C8.2, C9.2, C10.2, J1.1, J2.2, J2.4, R2.2, U3.4 (GND), U6.2 (VSS), U7.4 (P$V-)
unnamed: R1.2, R2.1, R3.2, U7.2 (-IN)
unnamed: U6.1 (VOUT), U7.3 (+IN)
SCL: J1.4, U6.5 (SCL)
SDA: J1.5, U6.4 (SDA)
TUNING_DAC_I2C_SELECT: J1.3, U6.6 (AO)
Vtune: J1.6, R1.1, R3.1, U7.1 (OUT)

Board: 2 copper layers, 17 parts (0 on the bottom side), 10 nets, no tracks yet.

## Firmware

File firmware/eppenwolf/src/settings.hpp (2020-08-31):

#define CORE_CLOCK_FREQ F_CPU

#define CORE_SUPPLY_VOLTAGE 3.3

#define ANALOG_WRITE_RESOLUTION 12
// #define ANALOG_WRITE_MAX_VAL (pow(2,ANALOG_WRITE_RESOLUTION)-1)
#define ANALOG_WRITE_MAX_VAL 4095

//mandated by DAC

#define ANALOG_READ_RESOLUTION 12
#define ANALOG_READ_MAX_VAL 4095



//
// #ifdef MOCK_INCLUDES
// #else
// #define DAC_write analogWrite
// #endif

#define BUTTON_PIN 16

#define DAC_MAX_VAL 4095

// #define MAX_MSG_SIZE  4096

#define HOST_BAUD_RATE 115200
#define DEBUG_BAUD_RATE 115200

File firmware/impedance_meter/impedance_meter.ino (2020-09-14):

const long frequencies[] = {2500,5000,10000,20000,40000};

const int num_freqs = 5;
const int num_wells = 8;
const int analog_input = A0;

int output_pins[8] = {2,3,4,5,6,7,8,9};

//cat /dev/ttyUSB7 | ts '%.s,'

void setup() {
  Serial.begin(115200);
  for(int i = 0; i < num_wells; i++){
    pinMode(output_pins[i], INPUT); //easier if on the same port
  }
}


void loop() {
  for(int f = 0; f < num_freqs; f++){
    for(int i = 0; i < num_wells; i++){
      pinMode(output_pins[i], OUTPUT);
      tone(output_pins[i], frequencies[f]);
      delay(50);
      long value = 0;
      for(int j = 0; j < 100; j++){
        value += analogRead(analog_input);
        delayMicroseconds(100);
      }
      value /= 100;
      noTone(output_pins[i]);
      pinMode(output_pins[i], INPUT);
      delay(50);
      Serial.print(i);
      Serial.print(',');
      Serial.print(frequencies[f]);
      Serial.print(',');
      Serial.println(value);
    }
  }
  delay(100);
}

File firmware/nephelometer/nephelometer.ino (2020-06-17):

#include <FreqCount.h>

const int VIS_transmittance_out = 0;
const int VIS_reflectance_out = 1;
const int IR_transmittance_out = 2;
const int IR_reflectance_out = 3;

void setup() {
  Serial.begin(115200);
  pinMode(VIS_transmittance_out, OUTPUT);
  pinMode(VIS_reflectance_out, OUTPUT);
  pinMode(IR_transmittance_out, OUTPUT);
  pinMode(IR_reflectance_out, OUTPUT);
  FreqCount.begin(100);
  delay(1000);
}

void all_off(){
  digitalWrite(VIS_transmittance_out, 0);
  digitalWrite(VIS_reflectance_out, 0);
  digitalWrite(IR_transmittance_out, 0);
  digitalWrite(IR_reflectance_out, 0);
}

signed long dark_corrected_sample(int pin){
  while (!FreqCount.available()); //wait until the next sample
  FreqCount.read(); //discard
  all_off();
  while (!FreqCount.available());
  unsigned long dark_count = FreqCount.read();  
  digitalWrite(pin, 1);
  while (!FreqCount.available());
  unsigned long light_count = FreqCount.read();  
)
  
  return (signed long)(light_count)-(signed long)dark_count;
}

void loop() { 
  signed long VIS_reflectance = dark_corrected_sample(VIS_reflectance_out);
  signed long VIS_transmittance = dark_corrected_sample(VIS_transmittance_out);
 
  signed long IR_reflectance = dark_corrected_sample(IR_reflectance_out);
  signed long IR_transmittance = dark_corrected_sample(IR_transmittance_out);
 
  Serial.print(VIS_reflectance);
  Serial.print(", ");
  Serial.print(VIS_transmittance);
  Serial.print(", ");
  Serial.print(IR_reflectance);
  Serial.print(", ");
  Serial.println(IR_transmittance);
//  Serial.print(",");
//  Serial.println(VIS_ratio,5);

}

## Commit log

2020-03-22 University mostly
    [insulator.scad, qucs.sch, roundedcube.scad]
2020-03-24 More re-organization of the shop, hit head sharply on a shelf
    [insulator.scad, insulator.stl, insulator2.scad, insulator2.stl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]
2020-04-01 Few changes
    [test.stl, test1.step, test_1.FCStd, uploads_fb_66_1d_9f_75_MountClamp-SCH40_PVC_3_4_inch.scad]
2020-04-02 Time to get methodical again.
    [test_1.FCStd]
2020-04-07 Just reorganized
    [qucs.sch]
2020-04-08 Mesh import partially working
    [local_oscillator_test.kicad_pcb]
2020-04-09 Import works
    [attenuator.sch, filter.sch, local_oscillator_test.kicad_pcb, local_oscillator_test_qucs.sch]
2020-04-09 Modelled reference oscillator, gprMax impulse model is looking fine
    [attenuator.sch, filter.sch, global.sch, local_oscillator_test.kicad_pcb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]
2020-04-09 Something resembling an impulse
    [local_oscillator_test.kicad_pcb, local_oscillator_test.sch]
2020-04-09 Trying a simple microstrip
    [NASA_oscillator.kicad_pcb, local_oscillator_test.kicad_pcb]
2020-04-10 Impulse functional, just needed to set ground plane
    [filter.sch, local_oscillator_test.kicad_pcb]
2020-04-10 Fixed boundary issue
    [NASA_oscillator.kicad_pcb]
2020-04-10 LO works!
    [filter.sch, local_oscillator_test.kicad_pcb, local_oscillator_test.sch, local_oscillator_test_qucs.sch]
2020-04-14 Phage propagation!
    [local_oscillator_test.kicad_pcb, local_oscillator_test.sch, nephelometer.FCStd, shaker_2.scad]
2020-04-21 Find neighbors
    [feedback_loop.sch]
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2020-04-26 Re-organization, focus back on microwave
    [attenuator.sch, feedback_loop.sch, global.sch, image_reject_filter.sch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]
2020-04-28 Crashed and burned there, but I think we're back.
    [downconverter-F.Cu.gbr, downconverter.kicad_pcb, downconverter.sch, image_reject_filter.kicad_pcb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]
2020-04-28 Downconverter board!
    [downconverter-F.Cu.gbr, downconverter.kicad_pcb]
2020-04-29 Phase shift simulation
    [feedback_loop.sch, image_reject_filter.sch]
2020-04-29 Feedback loop
    [feedback_loop.sch]
2020-04-29 Optimizer not working.
    [downconverter.kicad_pcb, feedback_loop.sch]
2020-04-29 Trying to optimize FB and phase shifter seperately
    [feedback_loop.sch]
2020-04-29 Pretty reasonable FB loop for the VCO
    [feedback_loop.sch]
2020-04-29 Cleaning up qucs
    [feedback_loop.sch]
2020-04-29 More qucs cleanup
    [feedback_loop.sch, image_reject_filter.sch]
2020-04-30 Feedback loop looks great now
    [feedback_loop.sch, local_oscillator.sch]
2020-05-01 Largely working feedback loop, but going to try phase shifter.
    [feedback_loop.sch, image_reject_filter.sch, local_oscillator.sch]
2020-05-01 Fb loop, small setback on varactor front
    [feedback_loop.sch]
2020-05-01 PIN diode Fb loop actually working
    [feedback_loop.sch, local_oscillator.sch]
2020-05-01 Upgrading kicad
    [feedback_loop.sch, local_oscillator.kicad_pcb, local_oscillator.sch]
2020-05-02 Somewhat altered fb loop
    [feedback_loop.sch, local_oscillator.kicad_pcb, local_oscillator.sch]
2020-05-03 Series inductor, possible X band downconversion?
    [feedback_loop.sch, local_oscillator-F_Cu.gbr, local_oscillator.kicad_pcb]
2020-05-04 Switched-line PINs, oh my!
    [feedback_loop.sch, phase_shifter.sch]
2020-05-04 Hybrid pin+varactor shifter
    [feedback_loop.sch, image_reject_filter.sch, phase_shifter.sch]
2020-05-04 Oh, of course - we don't need the LO swept!
    [feedback_loop.sch, local_oscillator-F_Cu.gbr, local_oscillator.kicad_pcb, local_oscillator.sch]
2020-05-05 Notch filter
    [feedback_loop.sch, local_oscillator-F_Cu.gbr, local_oscillator.kicad_pcb, local_oscillator.sch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]
2020-05-06 Doctest is awesome!
    [feedback_loop.sch, phase_shifter.sch]
2020-05-07 SIR filter sim functional!
    [SIR_unit_test.sch]
2020-05-07 Possibly switching SIR filter sim
    [SIR_unit_test.sch, feedback_loop.sch, phase_shifter.sch]
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2020-05-08 Isoelectric points!
    [H1N1.csv, H5N1.csv, T4_UP000009087_10665_all.fasta.pI.csv]
2020-05-09 A three-pole filter works almost perfectly.
    [comb_unit_test.sch, feedback_loop.sch]
2020-05-10 Filter optimization
    [optimize_filter_1.sch]
2020-05-10 Some words
    [optimize_filter_1.sch]
2020-05-11 Oh! discovered a bug, now the simply scaled filter works as expected
    [SIR_unit_test.sch, optimize_filter_1.sch]
2020-05-11 fuck filters
    [SIR_unit_test.sch, optimize_filter_1.sch]
2020-05-11 sir filter
    [optimize_filter_1.sch]
2020-05-11 Colpitts? huh
    [SIR_unit_test.sch, inductor_test.sch, local_oscillator.kicad_pcb, local_oscillator.sch]
2020-05-12 Man! This is looking good!
    [SIR_unit_test.sch, inductor_test.sch, optimize_filter_1.sch]
2020-05-12 Holy crap! almost there!
    [SIR_unit_test.sch]
2020-05-12 Perfect, again
    [SIR_unit_test.sch]
2020-05-12 Adding one more pole doesn't improve the range.
    [SIR_unit_test.sch]
2020-05-12 <chef's kiss>
    [SIR_unit_test.sch, local_oscillator.kicad_pcb, local_oscillator.sch]
2020-05-12 Rewrking board
    [SIR_unit_test.sch, local_oscillator.kicad_pcb, local_oscillator.sch]
2020-05-13 Hell yeah! DC biasing
    [SIR_unit_test.sch, charge_pump_biasing.sch, feedback_loop.sch, inductor_test.sch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]
2020-05-13 Next version!
    [SIR_unit_test.sch]
2020-05-14 Next rev.
    [SIR_unit_test.sch, inductor_test.sch, local_oscillator-F_Cu.gbr, local_oscillator.kicad_pcb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]
2020-05-15 I am being un-methodical. This must change.
    [SIR_unit_test.sch]
2020-05-15 Wrong phase shift.
    [SIR_unit_test.sch, feedback_loop.sch]
2020-05-15 truly the wrong phase entirely my dear
    [SIR_unit_test.sch]
2020-05-15 Optimization is promising
    [SIR_unit_test.sch, feedback_loop.sch, optimize_filter_1.sch]
2020-05-15 Fantastic tuning, slight improvement in phase shift needed
    [optimize_filter_1.sch]
2020-05-18 E. coli transfer
    [optimize_filter_1.sch]
2020-05-18 Microstrip gap
    [optimize_filter_1.sch]
2020-05-19 Two varactors in series
    [optimize_filter_1.sch]
2020-05-19 Backwards varactor
    [optimize_filter_1.sch]
2020-05-21 Apparent sweep!
    [optimize_filter_1.sch]
2020-05-21 Best one yet!
    [test.sch]
2020-05-22 simple lp
    [optimize_filter_1.sch, test.sch]
2020-05-23 paper progress
    [optimize_filter_1.sch]
2020-05-25 LO test something more
    [local_oscillator-F_Cu.gbr, local_oscillator.kicad_pcb, local_oscillator.sch, optimize_filter_1.sch]
2020-05-25 Setting up for LO test again
    [optimize_filter_1.sch]
2020-05-25 4-pole LO
    [local_oscillator.kicad_pcb, local_oscillator.sch, optimize_filter_1.sch]
2020-05-30 Testing python FDTD
    [transient_test.sch]
2020-05-30 SVG import improvements
    [local_oscillator.kicad_pcb, local_oscillator.sch]
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2020-05-31 Dump improvements, upgraded paraview
    [fdtd_test.kicad_pcb, fdtd_test.sch]
2020-05-31 Simplifying ports
    [fdtd_test.kicad_pcb]
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2020-06-03 looks okay, but doesn't agree with spice-only
    [input_terminated_new.tsv, output.tsv]
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2020-06-10 Some more documentation
    [fdtd_test.sch, wideband_LO.kicad_pcb, wideband_LO.sch]
2020-06-10 further fdtd
    [wideband_LO.kicad_pcb, wideband_LO.sch]
2020-06-10 LO progress
    [wideband_LO.kicad_pcb, wideband_LO.sch]
2020-06-10 Board design ostensibly complete
    [wideband_LO.kicad_pcb, wideband_LO.sch]
2020-06-11 FDTD kicad linkage
    [wideband_LO.kicad_pcb]
2020-06-11 Removed a few otherwise ignored parameters from the diode model
    [wideband_LO.kicad_pcb, wideband_LO.sch]
2020-06-11 Sources are shorting.
    [wideband_LO.sch]
2020-06-11 Sources still shorting
    [wideband_LO.kicad_pcb, wideband_LO.sch]
2020-06-11 Sim runs: ports not rotated.
    [wideband_LO.kicad_pcb, wideband_LO.sch]
2020-06-12 More fixes
    [wideband_LO.sch]
2020-06-13 Various sims
    [wideband_LO-F_Cu.gbr, wideband_LO.kicad_pcb]
2020-06-14 Reduced pad size, found bug with FDTD, etc, etc.
    [power_sensor.kicad_pcb, power_sensor.sch, wideband_LO.kicad_pcb, wideband_LO.sch]
2020-06-15 Buck-boost to linear
    [wideband_LO.kicad_pcb, wideband_LO.sch]
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2020-06-18 Replaced decoupling caps
    [driver_card.sch, wideband_LO.sch]
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2020-06-30 Fixed distribution; somewhat similar values
    [driver_card-F_Cu.gbr, driver_card.kicad_pcb, driver_card.sch]
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2020-10-25 Fixed PWM again, slide 0 re-done
    [fluorescence_data_cleaned.csv, fluorescence_data_slide_0.csv, fluorescence_data_slide_1.csv]
2020-10-25 green corrections
    [fluorescence_data_cleaned.csv, fluorescence_data_slide_0.csv, fluorescence_data_slide_1.csv]
2020-10-26 Green correction factors
    [fluorescence_data_slide_0.csv, green_corrections.csv]
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2020-11-09 Fixed erratic bug
    [slide_0.csv]
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2020-11-12 overwrote a bunch of data, reverting
    [fluorescence_slide_1.csv, phage_run_7_slide_0.csv]
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2020-11-12 data analysis mistake, conclusions are wrong
    [phage_run_7_slide_1.csv]
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2020-11-22 osmotically-stressed phage doesn't do it either
    [spectrum_water_1.csv]
2020-11-26 NLTL doesn't seem to help.
    [NLTL-6275.csv, NLTL-6275_cleaned.csv]
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2021-01-19 why's fdtd broken?
    [exposure_cell.sch]
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2021-04-15 DoF error
    [exposure_cell.sch]
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
